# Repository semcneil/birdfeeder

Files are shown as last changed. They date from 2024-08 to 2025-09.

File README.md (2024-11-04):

# BIRD FEEDER: Biometric Identification and Research-based Distribution Framework for Environmental Enrichment and Data-Enabled Ecological Research

## Overview
BIRD FEEDER, a collaborative effort between Embry-Riddle Aeronautical University, Prescott Campus (ERAU-PC), and the University of Georgia (UGA), epitomizes a multidisciplinary, multi-university initiative. This project, partially supported by a grant from the National Science Foundation (NSF), aims to create a bird feeder that is a cost-effective and solar-powered while engineered to detect, weigh, and selectively grant or deny access to food for specific bird species whose migratory patterns we wish to study. It merges technology with wildlife conservation, leveraging the diverse expertise of ERAU-PC’s engineering departments and UGA’s Warnell School of Forestry and Natural Resources.

## Introduction
This guide will take you through the steps of creating your very own Bird Feeder :)

## Installing Arduino
For this manual, we will be walking through the steps on how to use the Arduino IDE to write and upload code to the microcontroller powering your bird feeder. A future manual may be created to utilize the Arduino Cloud.

1.	Visit the official [Arduino website](https://www.arduino.cc)
2.	Click on the Software section at the top of the site.
3.	Under downloads, select the appropriate download option for your system.

**Windows:**
1.	Open the downloaded file to start the installation.
2.	You may be prompted with a security warning. If so, choose to run the installer.
3.	Follow the installation prompts. It’s usually safe to proceed with the default settings, but you can customize the installation location and components if needed.
4.	During the installation, you might be asked to install device drivers, accept, and install these drivers for Arduino boards to work properly with your computer.
5.	After installation, launch the Arduino IDE from your Start menu or desktop shortcut.

**Mac:**
1.	Open the downloaded .zip file to extract the Arduino application.
2.	Drag the Arduino application into your Applications folder.
3.	You might need to authorize the application due to macOS security preferences. You can do this in System Preferences > Security & Privacy.
4.	Open your Applications folder and double-click on the Arduino application to launch it.

**Linux:**
1.	Once downloaded, extract the tar archive to a location of your choice.
2.	Open a terminal and navigate to the extracted folder.
3.	Run the install.sh script to install the Arduino IDE. This can be done by executing ./install.sh from the terminal within the folder.
4.	You can start the Arduino IDE from your application menu or use the terminal to navigate to the installation directory and run ./Arduino.

## Installing Libraries
Installing libraries is an important step in ensuring that code runs as it should. Installing the wrong library may cause the code to behave strangely or not work at all.
**Libraries supported by Arduino:**
1.	With the Arduino IDE open, navigate to Tools > Manage Libraries. A menu should open from the left side of the window.
2.	In the Library Manager search bar, enter the name of the library and click install. This should install the latest version of the library.
3.	If it asks to Install Library Dependencies, select Install All. Libraries in the list below may appear as if they have already been installed, ignore them and continue installing the rest.

**For libraries unsupported by Arduino:**
1.	Download the library .zip file onto your computer.
2.	With the Arduino IDE open, navigate to Sketch > Include Library > Add .Zip Library…
3.	Find the library .zip file that you downloaded, select it, and select Open.

**Libraries to Install**

| Library Name | Author | Supported by Arduino?|
|--------------|--------|----------------------|
|SDFat - Adafruit Fork|Adafruit|Yes|
|Adafruit GFX Library| Adafruit| Yes|
|Adafruit AHTX0| Adafruit| Yes|
|Adafruit NAU7802 Library| Adafruit| Yes|
|RTClib| Adafruit| Yes|
|Boulder Flight Systems Circular Buffer| Brian Taylor| Yes|

## Ordering Parts
The code is developed to use these specific electronics. Ordering other electronics may result in unexpected consequences. Before ordering different parts, please consult with the Embry-Riddle Professors or modify the code to accommodate the changes.

|Part Name|Link|# of Parts Ordered per Unit|
|---------|----|---------------------------:|
|Mounting Grid|https://www.adafruit.com/product/5779|1|
|RFID Reader Kit| https://handsontec.com/index.php/product/hz-1050-wiegand-125khz-rfid-reader-kit/|1|
|Load Cell| https://www.sparkfun.com/products/14727|1|
|Load Cell ADC|https://www.adafruit.com/product/4538 |1|
|Mounting Screws & Standoff Set|https://www.adafruit.com/product/3299|1|
|STEMMA QT Cables|https://www.adafruit.com/product/4210|2|
|ESP32-S3 Feather|https://www.adafruit.com/product/5477|1|
|SD Add-on|https://www.adafruit.com/product/2922|1|
|Coin Cell Battery|https://www.adafruit.com/product/380|1|
|Stacking Headers|https://www.adafruit.com/product/2830|1|
|Female Headers|https://www.adafruit.com/product/2886|1|
|Temperature + Humidity Sensor|https://www.adafruit.com/product/4566|1|
|MicroSD Card|https://www.amazon.com/MicroSD-Memory-Class10-SDAdapter-Reader/dp/B07R3QRGGF|1|
|Jumper Wires|https://a.co/d/4cGIVyl|1|

*Note: Only 1 set of jumper wires is needed to build multiple units*

## Configuring the Arduino IDE
Now that we have the Arduino IDE and our ESP32 on hand installed we have to configure the options so that the code can be uploaded to our microcontroller.

1.	Connect the ESP32-S3 Feather 2MB PSRAM microprocessor to a computer via a USB-C cable.
2.	With the Arduino IDE open, navigate to Tools > Board: “There may be a board name here” > Boards Manager.
3.	In the Boards Manager search bar, enter the board name “esp32” and install the library labeled “esp32” by Espressif Systems.
4.	Select the board by navigating to Tools > Board: “There may be a board name here” > esp32 > Adafruit Feather ESP32-S3 2MB PSRAM board.
5.	Select the port you are connecting the microprocessor to the computer with by navigating to Tools > Port: “COM…” and selecting the COM port that is connected to the board. Typically, the “COM1” is not connected to the board on Windows OS.

Now we can begin uploading the code to the microprocessor.

## Uploading and Running Code
Please install libraries and configure the board before doing this step.
1.  Connect the ESP32-S3 Feather 2MB PSRAM microprocessor to a computer via a USB-C cable.
2.	Download the rtcLoggingWifi.ino file found in the rtcLoggingWifi folder found in the Austin Branch of this GitHub. The location of the most up to date .ino file will change in the future.
3.	Open Arduino IDE and open the sketch by navigating through File > Open and selecting the .ino file you just downloaded.
5.	To ensure that the code is working, select Sketch > Verify/Compile.
7.	To upload any code, the ESP32 has to be put into upload mode. While holding the Boot button (between the header and outgoing wire, labeled “Boot”), press and release the Reset button (labeled “Reset”). You can now release the Boot button.
8.	If the code compiled successfully, upload the code to the microprocessor by selecting Sketch > Upload.
9.	To run the program that was uploaded to the microcontroller, press the Reset button.
   
Since we haven't connected any of the other components this will likely fail or do nothing. Steps 7-9 are still important though because after installing all the electronics, it will be difficult to access the USB-C port on the microcontroller.

## Wiring the Electronics
The order in which you connect the electronics should not matter. For the STEMMA QT Cable ensure that it is properly oriented by checking that the holes at the end of the cable match the pins in the ports.
1.	Connect a STEMMA QT Cable to the microcontroller and the Load Cell ADC. The connection point can be found near the center of the board. The connection point for the Load Cell ADC is found on either end of the board.
3.	Insert 3 wires into the headers (The black piece of plastic on top of the board with a series of holes) found on the microcontroller. The wires go into the GND, USB, and RX pins of the header.
4.	On the RFID Reader board, connect the following wires to the following pins: GND wire to GND pin, USB wire to 5V pin, and RX wire to TX0 pin.

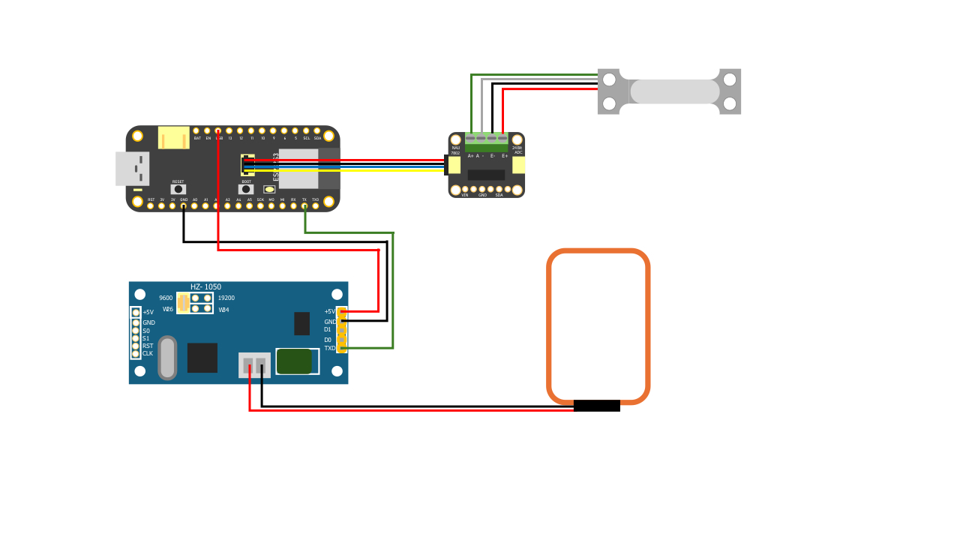
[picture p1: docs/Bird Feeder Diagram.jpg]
Wiring Diagram
||
|:-:|
| *Basic Diagram of the wiring layout for the base components in the BIRD FEEDER* |

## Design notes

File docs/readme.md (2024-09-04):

This folder contains the documentation and support files

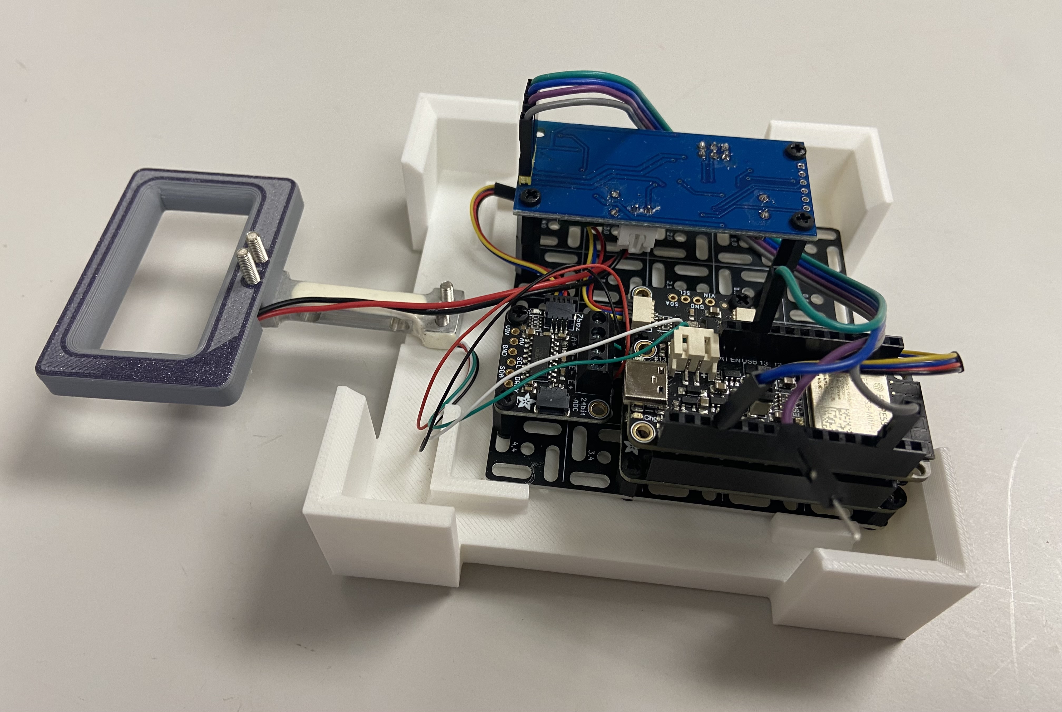
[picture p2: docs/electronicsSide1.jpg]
Electronics setup
||
|:-:|
| *Electronics board* |

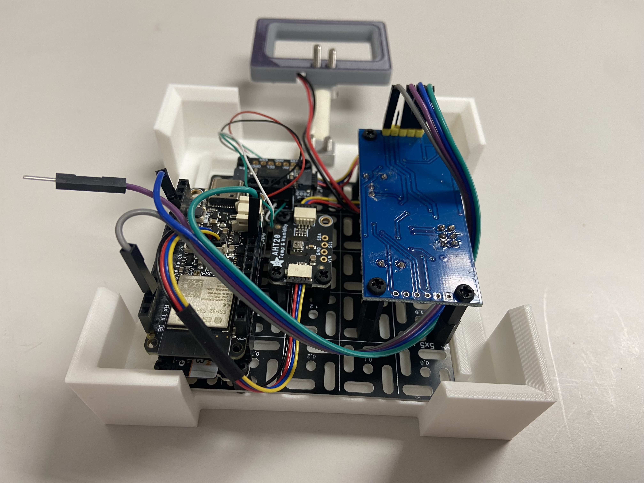
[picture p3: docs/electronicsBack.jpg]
Electronics setup
||
|:-:|
| *Electronics board* |

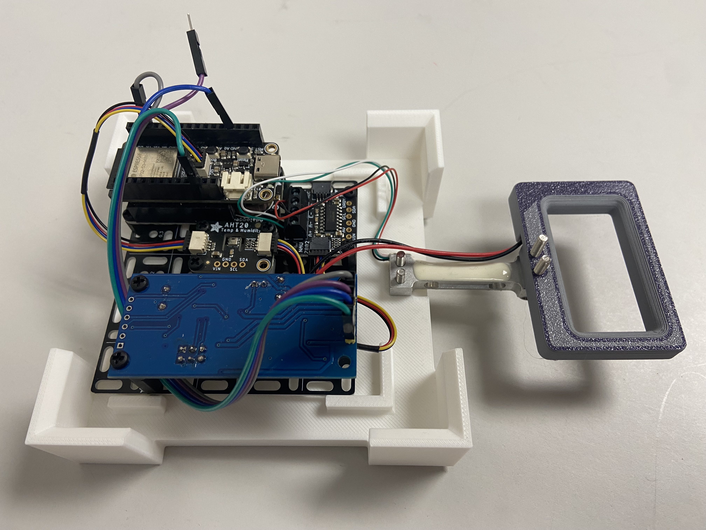
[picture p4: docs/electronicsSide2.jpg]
Electronics setup
||
|:-:|
| *Electronics board* |

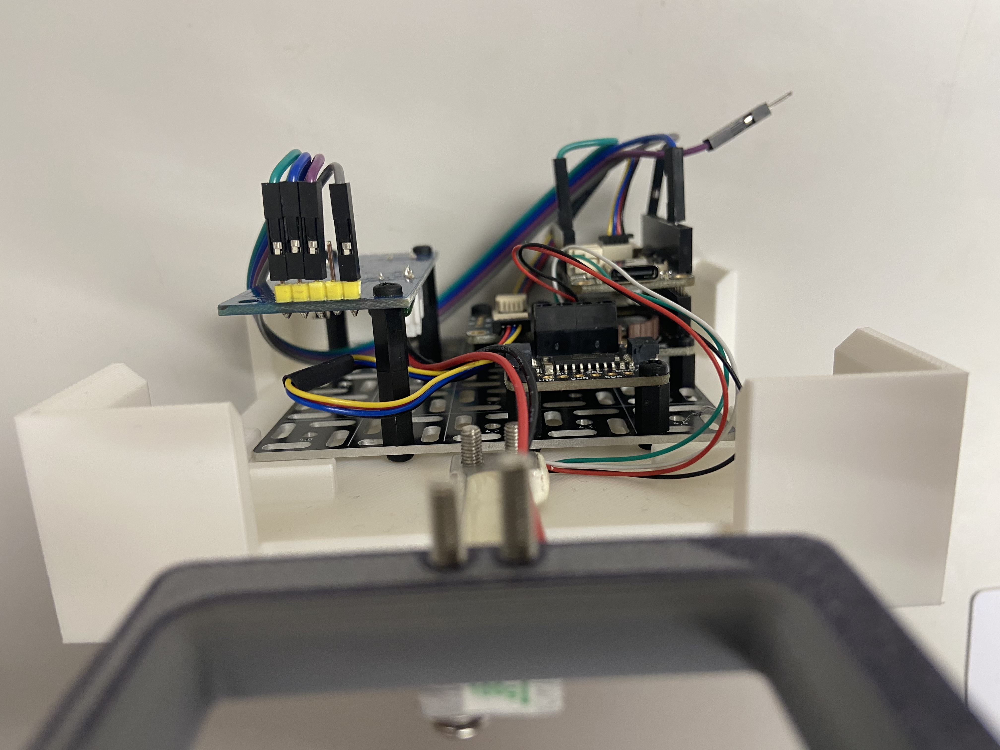
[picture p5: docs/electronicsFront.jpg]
Electronics setup
||
|:-:|
| *Electronics board* |

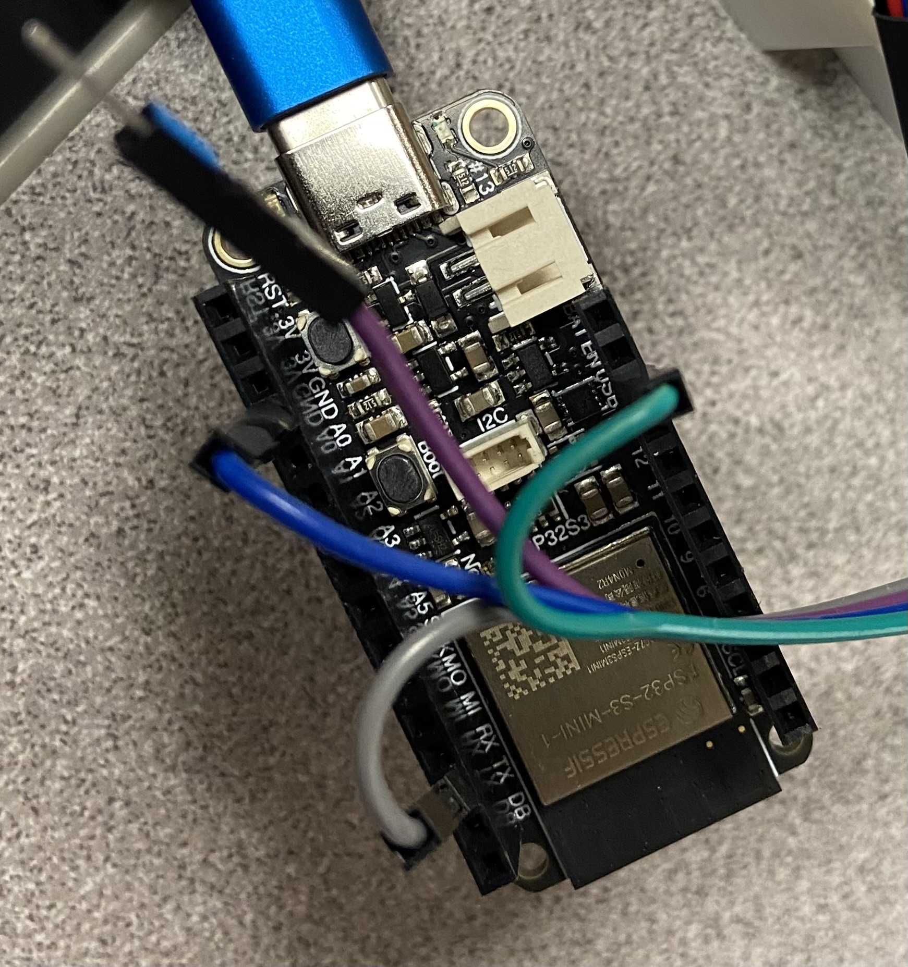
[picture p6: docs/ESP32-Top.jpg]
||
|:-:|
| *ESP-32 top wiring* |

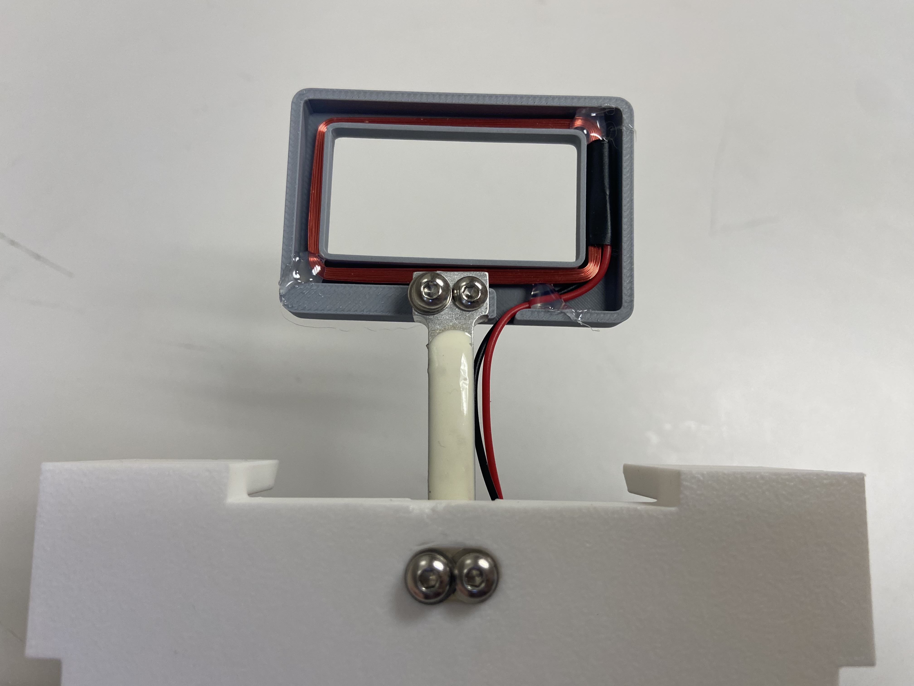
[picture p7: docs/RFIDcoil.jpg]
RFID coil setup
||
|:-:|
| *RFID coil assembly* |

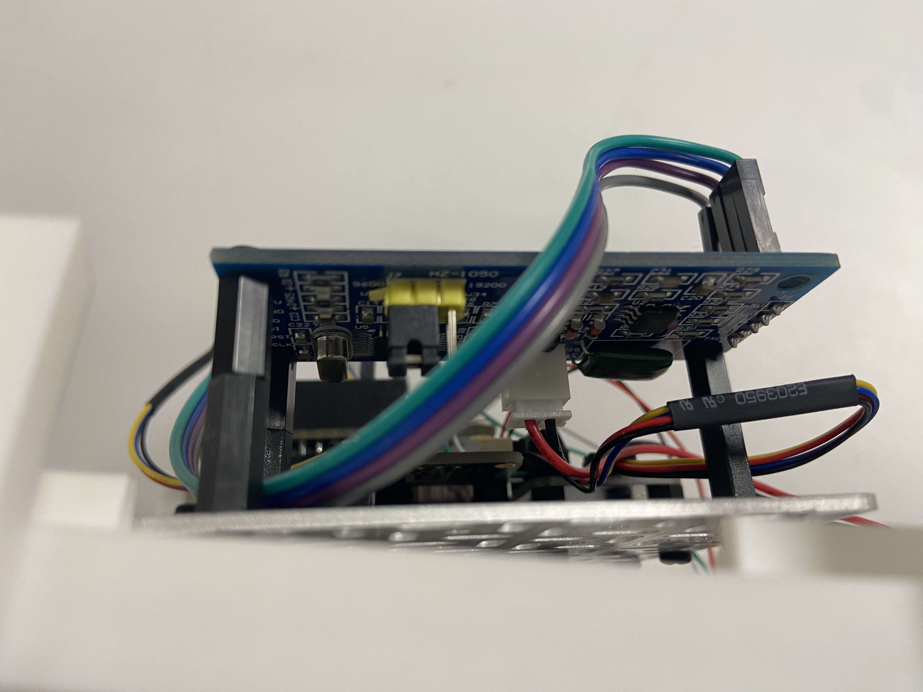
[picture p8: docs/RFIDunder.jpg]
RFID coil setup
||
|:-:|
| *Underneath the RFID circuit board* |

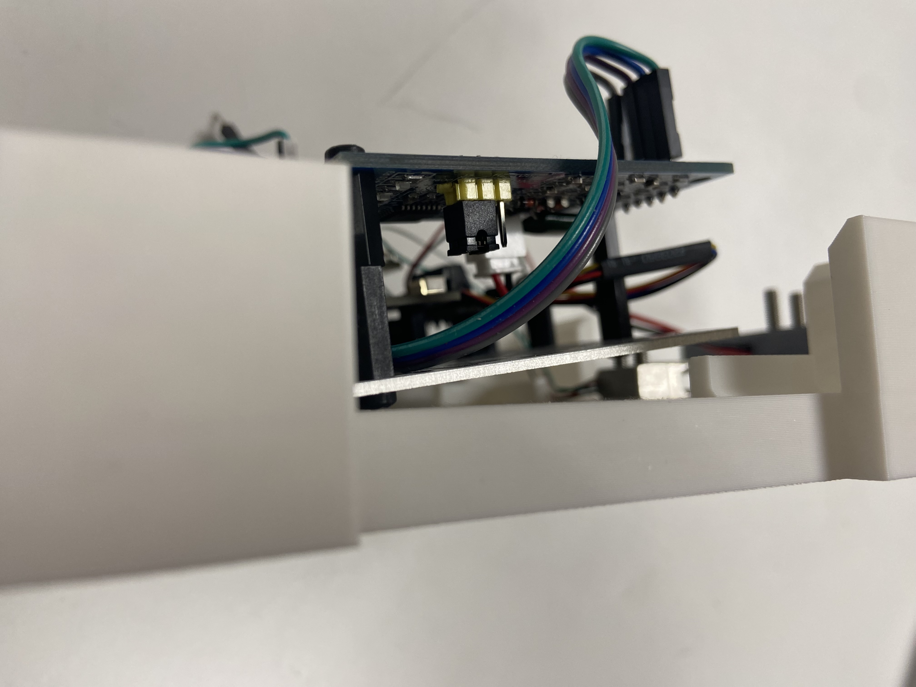
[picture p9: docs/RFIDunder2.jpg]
RFID coil setup
||
|:-:|
| *Underneath the RFID circuit board* |

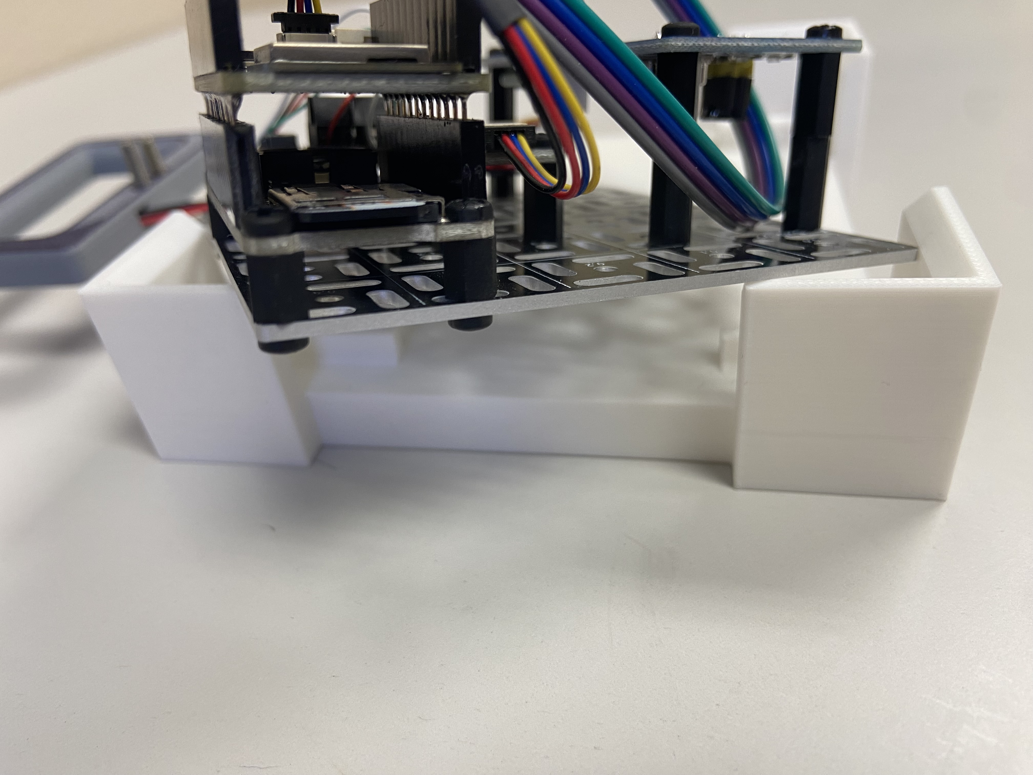
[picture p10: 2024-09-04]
docs/logger.jpg

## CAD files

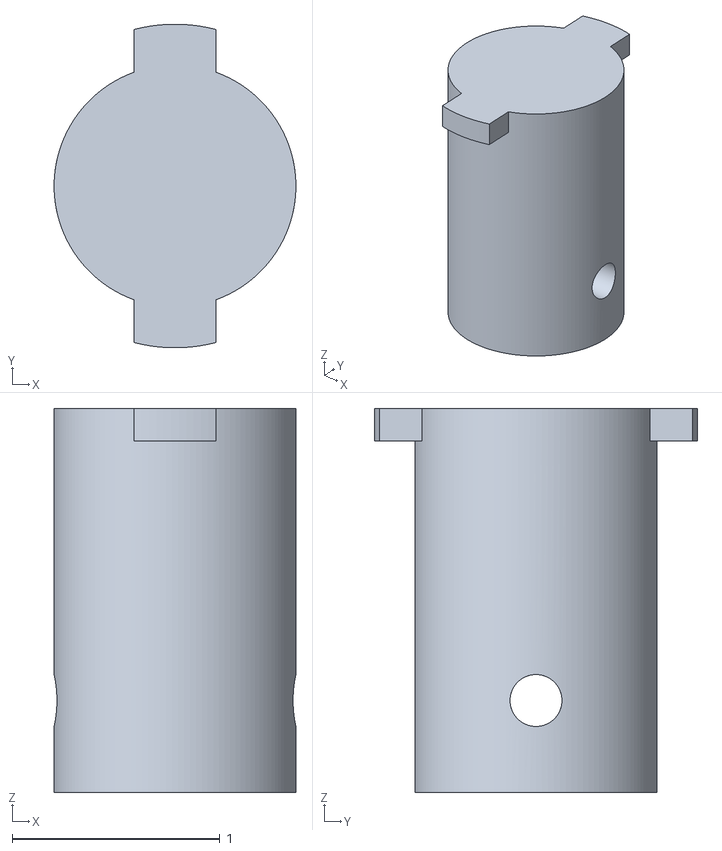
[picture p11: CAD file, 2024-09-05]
printFiles/Cap pole mount- 4.5.stl
1.17 x 1.56 x 1.85

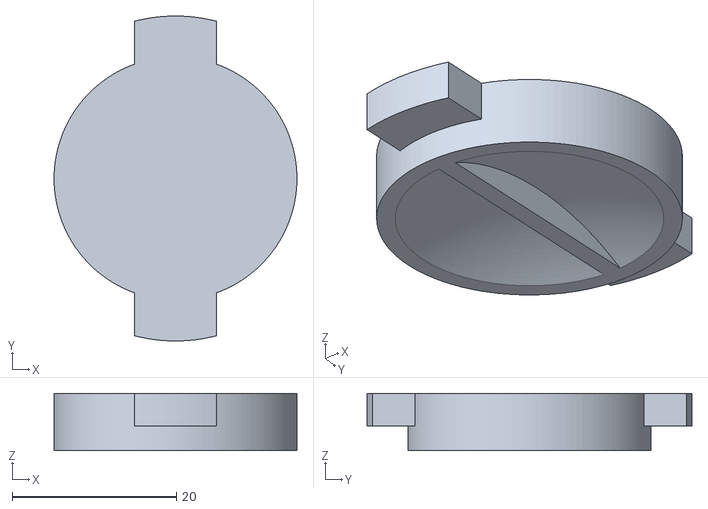
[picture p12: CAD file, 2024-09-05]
printFiles/Cap - 4.5.stl
29.6 x 39.6 x 7.00

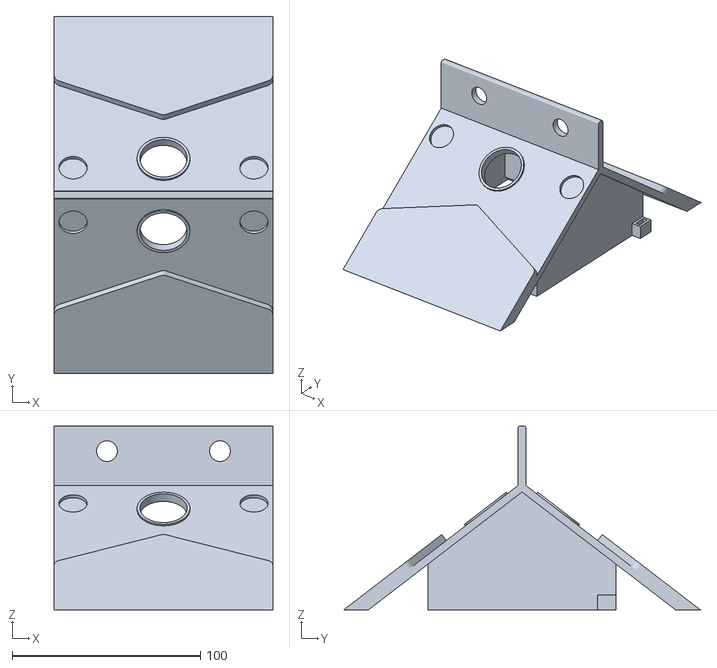
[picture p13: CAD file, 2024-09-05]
printFiles/Roof - 4.7.stl
116.0 x 189.5 x 97.6

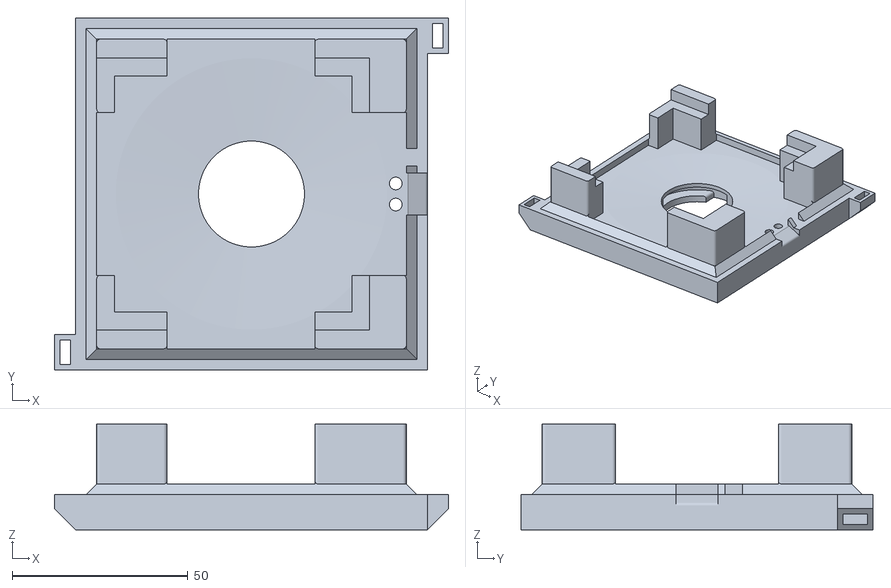
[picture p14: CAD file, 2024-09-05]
printFiles/Floor - 4.5.stl
112.0 x 100.0 x 30.0

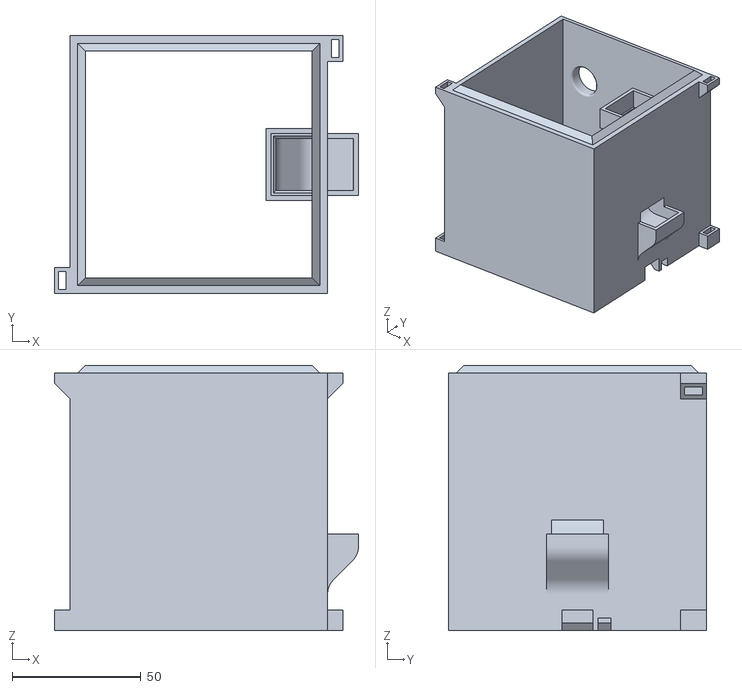
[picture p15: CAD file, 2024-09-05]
printFiles/Bottom - 4.5.stl
118.0 x 100.0 x 103.0

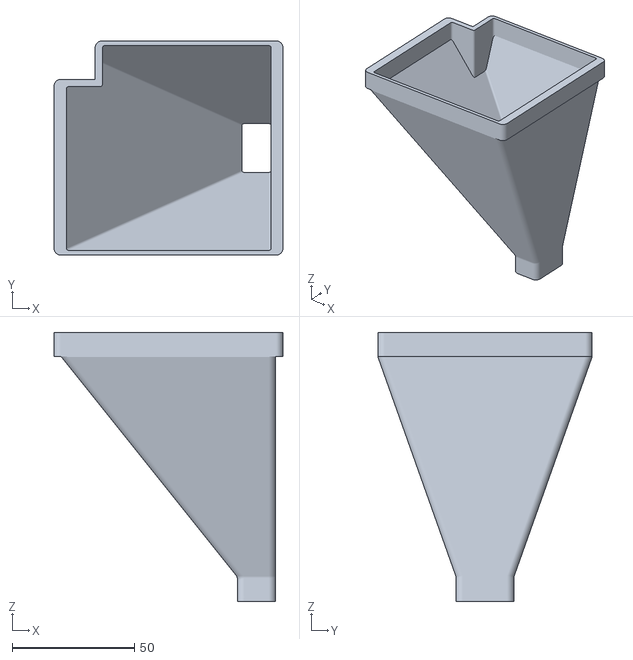
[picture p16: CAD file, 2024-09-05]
printFiles/Chute - 4.5.stl
93.6 x 87.6 x 110.0

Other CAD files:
printFiles/Top - 4.6.stl

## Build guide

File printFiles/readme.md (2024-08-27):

# Files to 3D print the bird feeder physical parts go here

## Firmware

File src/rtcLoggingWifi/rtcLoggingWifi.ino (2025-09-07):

/* rtcLoggingWifiRevisionNine.ino

   This version refines all the methods to have similar syntax and error handling
   It also adds interaction with the settings file on the SDCard. It allows allows for the inital settings of the board
   This version also fixes the RTC allowing for proper time tracking and adjustment.
   This version also propely interprets data nad gives correct output. 
   This version meets all project specifications 
   April 18th 2025
*/
#include "esp_system.h"
#include <SPI.h>    // SD card
#include <SdFat.h>  // Adafruit fork of SdFat for SD card
#include <WiFi.h>   
#include <WiFiClient.h>
#include <WebServer.h>
#include <ESPmDNS.h>
#include <Adafruit_GFX.h>
#include <Adafruit_AHTX0.h>    // temp/humidity
#include <Adafruit_NAU7802.h>  // load cell ADC
#include "RTClib.h"            // Real-time clock (PCF8523)
#include "circle_buf.h"        // circular buffer (Boulder Flight version)
#include <PCA9536D.h>
#include <Wire.h>
#include <Adafruit_INA219.h>
#include "Adafruit_BMP3XX.h"
#include "Adafruit_MLX90393.h"
#include <NTPClient.h>
#include <WiFiUdp.h>
#include "esp_sleep.h"
//The following variables can be changed and modified to manipulate data gathering and other stats.
const int wifiMaxCheckTimes = 10;       //Max Times Wifi is checked. Default Value: 10
int timeZone = -4;                       //Timezone. Default is UTC-0
const int loopsBetweenReads = 10;       //If a tag is read and it is the same as the last tag read, wait this many loops before logging it again. Default is 10.
const int loadCellBufferSize = 3;       //How many values priror to a tag being read are logged. Default: 3
const int loopsBetweenTimeLogs = 1000;  //How many loops between logging the time and tempature. Default is 10000;
const char* feederName = "feederOne";   //Name of the feeder, change freely
const int maxReadingCount = 50;
//Macey adds here- variables added and manipulated to change the deep sleep timer
const unsigned long startSleepTime = 36000000; //convert the hour you want the sleep to start to milliseconds, current 10 pm 
const unsigned long endSleepTime = 18000000; //concert the hour you want to wake in milliseconds, current 5 AM
//unsigned long lastAwakeTime = 0; 
RTC_DATA_ATTR unsigned long lastWakeUpTime = 0; //storing the time in RTC memory
unsigned long timeToFive = 0; //amount of time left sleeping until 5 AM
unsigned long currentTimeForSleep = 0; //storing the current time , currentMilis
//end Macey adds
//The following variables can be modified to manipulate the web server.
const char* default_ssid = "Wesley's Cooler Hotspot";
const char* default_password = "frogsarecool";
const char* default_apssid = "birdfeeder";
const char* default_appassword = "password1";
char ssid[32];
char password[32];
char apssid[32];
char appassword[32];

//Variables beyong this point should NOT be modified unless specified elsewhere
String tagNum = "";
String lastTagRead = "";
String readingId = "";
int loopsSinceLastRead = 0;
int loopCount = 0;
int readingCount = 0;
int loadCellBuffer[loadCellBufferSize];

#define SD_CS 10       // SD card chip select
#define I2C_PWR_PIN 7  // pin to turn on/off I2C power, set high for on
SdFat SD;              // required with SdFat.h, not SD.h
SdFile myFile;         // not sure why SdFile and not just File
File32 myFileLoadCell;
File32 myFileHousekeeping;
File32 myFileTempature;
String fname = "/settings.txt";  // forward slash critical for ESP32 function
String fname2;
String fname3;
String baseName = "/data";
String ext = ".csv";
String settingFname = "/settings.txt";  // forward slash critical for ESP32 function
int lastFileNum = 0;
Adafruit_NAU7802 nau;  // load cell
Adafruit_AHTX0 aht;    // Temperature / humidity
RTC_PCF8523 rtc;

#define BMP_SCK 13
#define BMP_MISO 12
#define BMP_MOSI 11
#define BMP_CS 10

#define MLX90393_CS 10

Adafruit_INA219 solar1(0x40);
Adafruit_INA219 solar2(0x44);
Adafruit_INA219 onlyPwr(0x42);
Adafruit_INA219 dataPwr(0x45);
#define BATT_LOG_PERIOD 5000  // ms between battery logs

PCA9536 buzzLED;
#define RED 0
#define GRN 1
#define BLU 2
#define BUZZ 3

Adafruit_BMP3XX bmp;

Adafruit_MLX90393 sensor = Adafruit_MLX90393();

WiFiUDP ntpUDP;
NTPClient timeClient(ntpUDP);

struct loadPoint {
  DateTime t;
  int32_t load;
  unsigned long millis;
};

WebServer *server0, *server1, *server2;

#ifdef LED_BUILTIN
const int led = LED_BUILTIN;
#else
const int led = 13;
#endif


/* This method adds padding zeros to ensure data is the same size 
*/
String zeroPad(int ii) {
  String outStr = "";
  if (ii < 10) {
    outStr += "0";
  }
  outStr += String(ii);
  return (outStr);
}


/* This method handles the web servers and gives visual feedbakc for this
*/
void handleRoot(WebServer* server,
                const String& content) {
  digitalWrite(led, 1);
  server->send(200, "text/html", content);
  digitalWrite(led, 0);
}

/*Method for handling downloads
*/
void handleDownload0() {
  // check that an argument of type filename has been submitted
  if (server0->args() < 1) {
    server0->send(200, "text/plain", "Need argument of type ?filename=somename.csv");
    return;
  }
  // get the size of the file
  // create the response with the file contents
  String fnameNew = "junk.txt";
  for (int ii = 0; ii < server0->args(); ii++) {
    Serial.println("Arg " + String(ii) + " -> ");
    Serial.println(server0->argName(ii) + ": ");
    Serial.println(server0->arg(ii) + "\n");
    if (server0->argName(ii) == "filename") {
      fnameNew = "/";  // very important for ESP32 based filenames
      fnameNew += server0->arg(ii);
      break;
    }
  }
  Serial.println("Downloading file: " + fnameNew);
  File32 fptr;  // = SD.open(fname.c_str());

  if (!fptr.open(fname.c_str(), O_RDONLY)) {
    // file doesn't exist
    Serial.println("File " + fnameNew + " doesn't exist");
    server0->send(200, "text/plain", "File " + fnameNew + " doesn't exist");
    return;
  }
  Serial.println("Filesize " + String(fptr.fileSize()));
  server0->streamFile(fptr, "text/plain");
}

/* handleFileExample0

   This shows how to process arguments and create
   a file that the client will be asked to download.
   It expects a URL like: 
   http://birds.local:8080/file?asdf=5&something=else
*/
void handleFileExample0() {
  String message = "";
  message += "# args: ";
  message += server0->args();
  message += "\n";
  for (int ii = 0; ii < server0->args(); ii++) {
    message += "Arg " + String(ii) + " -> ";
    message += server0->argName(ii) + ": ";
    message += server0->arg(ii) + "\n";
  }
  server0->sendContent("HTTP/1.1 200 OK\n");
  server0->sendContent("Content-Type: text/plain\n");
  server0->sendContent("Content-Disposition: attachment; filename=junk.txt\n");
  server0->sendContent("Content-Length: " + String(message.length()) + "\n");
  server0->sendContent("Connection: close\n");
  server0->sendContent("\n");  // to indicate headers have ended
  // server0->sendHeader("Content-Disposition", "attachment; filename=junk.txt");
  server0->sendContent(message);
  // server0->send(200,"text/plain", message.c_str());
}

void handleRoot0() {
  String outStr = "<html><head><title>Bird Files</title></head><body><h1>Files</h1><br>\n";
  outStr += "<strong>Local Access Point:&nbsp;</strong>";
  outStr += apssid;
  outStr += "<br>\n<strong>Local Access Point Password:&nbsp;</strong>";
  outStr += appassword;
  outStr += "<br><br>\n\n<strong>WiFi AccessPoint: </strong>";
  outStr += ssid;
  outStr += "<br>\n<strong>WiFi Access Point Password: </strong>";
  outStr += password;
  outStr += "<br><br>\n\n";

  File32 rootDir = SD.open("/");
  while (true) {
    File32 entry = rootDir.openNextFile();
    if (!entry) {
      outStr += "No more files<br><br>\n";
      outStr += "<strong>Edit Real-Time-Clock</strong><br><br>"
                "<form action=\"/rtcForm\" method=\"get\">"
                "<label for=\"rtcValue\">MM/DD/YYYY HH:MM:SS:</label>"
                "<input type=\"text\" id=\"rtcValue\" name=\"rtcValue\">"
                "<input type=\"submit\" value=\"Submit\">"
                "</form>"
                "<br>"
                "<form action=\"/timeZoneForm\" method=\"get\">"
                "<label for=\"timeZoneValue\">Timezone UTC(#):</label>"
                "<input type=\"text\" id=\"timeZoneValue\" name=\"timeZoneValue\">"
                "<input type=\"submit\" value=\"Submit\">"
                "</form>"
                "<br>"
                "<strong>Edit settings.txt</strong> (Restart ESP32-S3 to apply changes)"  // Too lazy to implement a better fix
                "<br><br>"
                "<form action=\"/wifiSSIDForm\" method=\"get\">"
                "<label for=\"wifiSSIDValue\">WiFi Access Point SSID:</label>"
                "<input type=\"text\" id=\"wifiSSIDValue\" name=\"wifiSSIDValue\">"
                "<input type=\"submit\" value=\"Submit\">"
                "</form>"
                "<br>"
                "<form action=\"/wifiPasswordForm\" method=\"get\">"
                "<label for=\"wifiPasswordValue\">WiFi Access Point Password:</label>"
                "<input type=\"text\" id=\"wifiPasswordValue\" name=\"wifiPasswordValue\">"
                "<input type=\"submit\" value=\"Submit\">"
                "</form>"
                "<br>"
                "<form action=\"/apSSIDForm\" method=\"get\">"
                "<label for=\"apSSIDValue\">Local Access Point SSID:</label>"
                "<input type=\"text\" id=\"apSSIDValue\" name=\"apSSIDValue\">"
                "<input type=\"submit\" value=\"Submit\">"
                "</form>"
                "<br>"
                "<form action=\"/apPasswordForm\" method=\"get\">"
                "<label for=\"apPasswordValue\">Local Access Point Password:</label>"
                "<input type=\"text\" id=\"apPasswordValue\" name=\"apPasswordValue\">"
                "<input type=\"submit\" value=\"Submit\">"
                "</form>"
                "<br>"
                "<form action=\"/restart\" method=\"post\">"  // Teehee (Late Night Delerium Hittin HARD)
                "<input type=\"submit\" value=\"Restart ESP32\">"
                "</form>";
      outStr += "</body></html>";
      break;
    }
    char nameField[16];  //  Allows files with names less than 16 characters. Perhaps should be upped to 32?
    int nameLen = entry.getName(nameField, 16);
    if (nameLen > 0 && nameField[0] != '.') {
      uint16_t mDate = 0;
      uint16_t mTime = 0;
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

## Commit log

2024-09-05 Added STL files
    These are the 3D print files for the bird feeder
    [Bottom - 4.5.stl, Cap - 4.5.stl, Cap pole mount- 4.5.stl, Chute - 4.5.stl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]
2024-09-30 Update README.md
    Added Wiring Diagram
    Removed Mounting Section
